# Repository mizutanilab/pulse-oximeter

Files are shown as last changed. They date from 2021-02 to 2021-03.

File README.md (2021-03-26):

# Pulse-oximeter using MAX30102, AAA battery-powered <BR><BR>パルスオキシメーター MAX30102 使用，単４電池駆動
Of course, it's home brewed. もちろん自作です。<br>
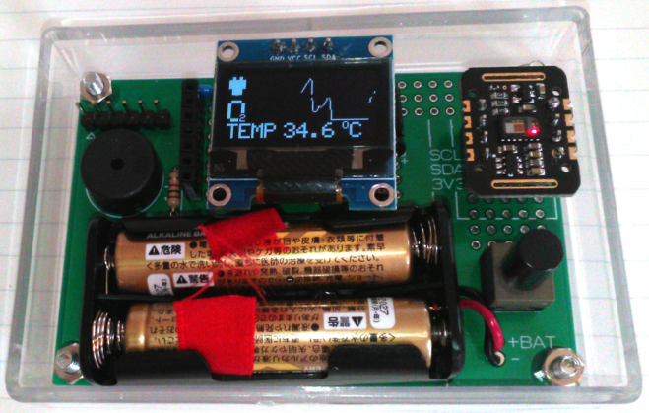
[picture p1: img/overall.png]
overall

  
## Display 表示
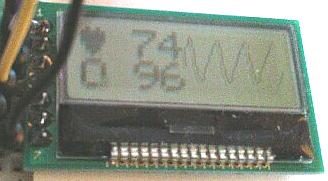
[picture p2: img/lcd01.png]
LCD
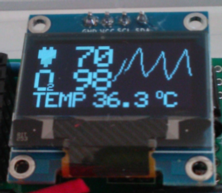
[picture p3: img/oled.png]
OLED
 
<BR>
Obviously, I'm alive. 明らかに生きてます。<BR><BR>

## Schematic 回路図
Nothing special. 普通です。<BR>
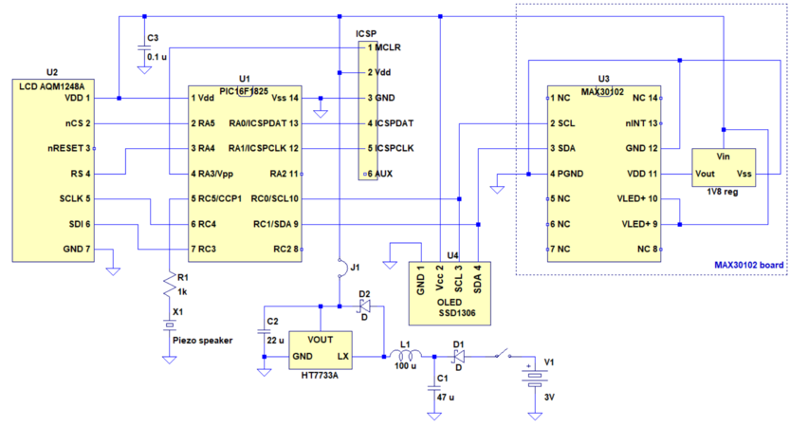
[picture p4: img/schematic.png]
schematic

<BR><BR>

## PCB 基板
Gerber files are <A href="gerber/">here</a>. ガーバーファイルは<a href="gerber/">ここ</a>です。<BR>
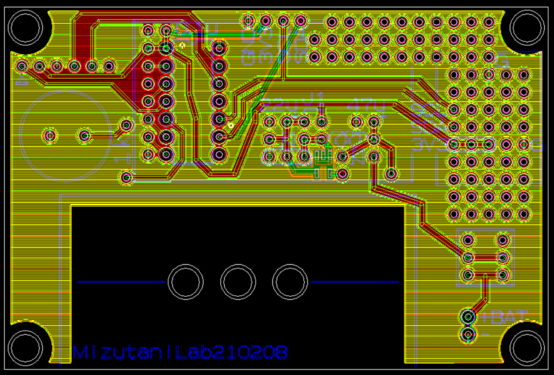
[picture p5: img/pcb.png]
pcb

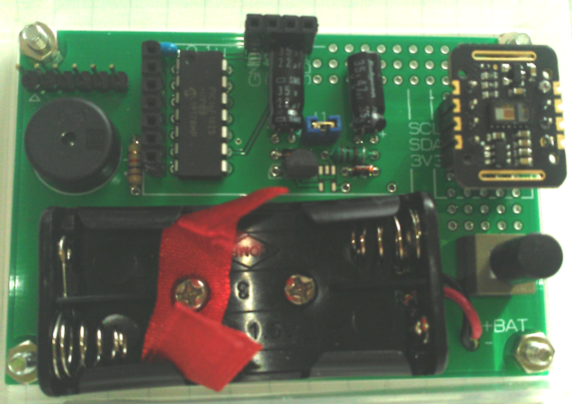
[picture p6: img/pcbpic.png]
pcb_picture

<BR><BR>

## BOM 部品表
<table>
<tr><th>Item</th><th>Description</th><th>Brand</th><th>QTY</th></tr>
<tr><td>Sensor</td><td>MAX30102 breakout</td><td>Maxim Integrated, etc</td><td>1</td></tr>
<tr><td>MCU</td><td>PIC16F1825-I/P</td><td>Microchip</td><td>1</td></tr>
<tr><td>Display</td><td>OLED with SSD1306<BR>or AQM1248A</td><td>Sunhokey, etc<BR>Akizuki</td><td>1</td></tr>
<tr><td>3V3 boost conv</td><td>HT7733A (TO-92)<BR>or TPS613221ADBV, etc</td><td>Holtek<BR>TI</td><td>1</td></tr>
<tr><td>Schottkey D</td><td>SD103A</td><td>PANJIT or Vishay</td><td>2</td></tr>
<tr><td>Piezo speaker</td><td>PKM13EPYH4000-A0</td><td>muRata</td><td>1</td></tr>
<tr><td>L</td><td>100 uH</td><td>-</td><td>1</td></tr>
<tr><td>C</td><td>47 uF electrolytic</td><td>-</td><td>1</td></tr>
<tr><td>C</td><td>22 uF electrolytic</td><td>-</td><td>1</td></tr>
<tr><td>C</td><td>0.1 uF ceramic</td><td>-</td><td>1</td></tr>
<tr><td>R</td><td>1k ohm</td><td>-</td><td>1</td></tr>
<tr><td>SW</td><td>3p toggle or alternate push</td><td>-</td><td>1</td></tr>
<tr><td>Battery box</td><td>AAA x 2</td><td>-</td><td>1</td></tr>
<tr><td>Pin header</td><td>6 pin (ICSP)</td><td>-</td><td>1</td></tr>
<tr><td>Pin header & jumper</td><td>2 pin</td><td>-</td><td>1 each</td></tr>
<tr><td>Pin socket</td><td>7 pin (LCD) or 4 pin (OLED)</td><td>-</td><td>1</td></tr>
<tr><td>Pin socket</td><td>4 pin (MAX30102 board)</td><td>-</td><td>1-2</td></tr>
<tr><td>PCB</td><td>custom</td><td>-</td><td>1</td></tr>
<tr><td>Nuts & bolts</td><td>M3 x 10 mm</td><td>-</td><td>4 sets</td></tr>
<tr><td>Nuts & bolts</td><td>M2.6 x 6 mm</td><td>-</td><td>1-2 sets</td></tr>
<tr><td>Spacer</td><td>3 mm x 3 mm height, resin</td><td>-</td><td>4</td></tr>
<tr><td>Enclosure</td><td>85.5 x 59 x 24 mm, ABS</td><td>Akizuki</td><td>1</td></tr>
</table>
It's less than 25 US$ in total. MAX30102 breakout board with a 1.8V regulator is available from Maxim (MAXREFDES117#) and also from 3rd parties. MAX30101 board can also be used. There are two display options: OLED with SSD1306 and LCD AQM1248A with ST7565R. Choose one of them using #define directive. HEX binary for each display is available. HT7733A is a DC/DC boost converter, which can be substituted with TPS613221ADBV, TPS61097A-33DBV, MAX1724EZK33, or XC9142B33CMR-G. Surface mount pads for these devices are prepared, but not tested. If you use a substitute converter, L/C arrangements and their constants should also be reexamined accroding to datasheet recommendations. You may need a 6-pin male-to-female DuPont wire to connect this PCB to a PIC programmer.<BR><BR>
全部で2500円いきません。MAX30102ボードはMaximのMAXREFDES117#などいくつかの種類が入手可能です。MAX30101のでも使えます。ディスプレイは、秋月グラフィックLCDか、SSD1306のOLEDを選べます。ソースコードの#define文で設定してください。HEXファイルはどちらも用意しています。おもて面のパッドはTPS613221ADBVなどHT7733Aの代替品用で、SOTパッケージのHT7733Aには使えません。センサはアマゾンで、それ以外は秋月で手に入ります。基板をPICプログラマーにつなぐには、6pオスメスケーブル（共立電子QIケーブル6S-6Pなど）も必要です。
<BR>

## SpO<sub>2</sub> calculation 計算式
Four options are implemented. Default is option 1.<BR>
4つあります。既定では1です。<BR>
  1. SpO<sub>2</sub> = -33.437 <i>R</i> + 114.9 (linear approximation of Reynolds et al. (1991) Br J Anaesth 67, 638)<BR>
  2. SpO<sub>2</sub> = -17 <i>R</i> + 104 (User guides & manuals 6409, Maxim Integrated)<BR>
  3. SpO<sub>2</sub> = 1.5958422 <i>R</i><sup>2</sup> -34.6596622 <i>R</i> + 112.6898759 (Application note 6845, Maxim Integrated)<BR>
  4. SpO<sub>2</sub> = -45.060 <i>R</i><sup>2</sup> + 30.354 <i>R</i> + 94.845 (MAX3010x sensor library, SparkFun)<BR>
where <i>R</i> = (AC<sub>red</sub> / DC<sub>red</sub>) / (AC<sub>IR</sub> / DC<sub>IR</sub>).<BR><BR>
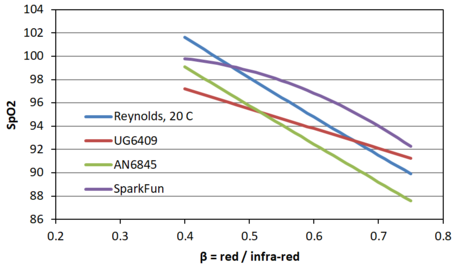
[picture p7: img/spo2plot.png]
spo2models
 <a href="spo2models.xlsx">Excel file</A><BR>

## References 参考
Reynolds et al. (1991) Br J Anaesth 67, 638-643. <a href="https://doi.org/10.1093/bja/67.5.638">DOI</A><BR>
Recommended Configurations and Operating Profiles for MAX30101/MAX30102 EV Kits, <a href="https://www.maximintegrated.com/en/design/technical-documents/userguides-and-manuals/6/6409.html">User guides & manuals 6409</a>, Maxim Integrated<BR>
Guidelines for SpO2 Measurement Using the MaximR MAX32664 Sensor Hub, <a href="https://www.maximintegrated.com/en/design/technical-documents/app-notes/6/6845.html">Application note 6845</a>, Maxim Integrated<BR>
MAX3010x sensor library, SparkFun. <a href="https://github.com/sparkfun/SparkFun_MAX3010x_Sensor_Library">GitHub</a><BR>

## DISCLAIMER お断り
This repository is provided "AS IS", without warranty of any kind, either express or implied. Use it on your own responsibility.<BR>
このリポジトリは「そのまま」で提供されており、明示・暗示を問わず、いかなる保証もありません。ご利用はご自身のご責任でどうぞ。

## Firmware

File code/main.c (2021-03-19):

/* Pulse oximeter 
 * Sensor: MAX30102
 * MCU: PIC16F1823
 * OLED: SSD1306
 * LCD: ST7565R / AQM1248
 * 2021 (C) Mizutani Lab
 */

#include <htc.h>
#include "lcd.h"
#include "i2c.h"
#include "oled.h"

//#define DISP_LCD
#define DISP_OLED

#define MAX30102_INTR_STAT1 0x00
#define MAX30102_INTR_STAT2 0x01
#define MAX30102_INTR_EN1 0x02
#define MAX30102_INTR_EN2 0x03
#define MAX30102_FIFO_WR_PTR 0x04
#define MAX30102_OVF_COUNTER 0x05
#define MAX30102_FIFO_RD_PTR 0x06
#define MAX30102_FIFO_DATA 0x07
#define MAX30102_FIFO_CONFIG 0x08
#define MAX30102_MODE_CONFIG 0x09
#define MAX30102_SPO2_CONFIG 0x0A
#define MAX30102_LED1_PA 0x0C
#define MAX30102_LED2_PA 0x0D
//#define MAX30105_PILOT_PA 0x10
#define MAX30102_MULTI_LED_CTRL1 0x11
#define MAX30102_MULTI_LED_CTRL2 0x12
#define MAX30102_TEMP_INT 0x1F
#define MAX30102_TEMP_FRAC 0x20
#define MAX30102_TEMP_CONFIG 0x21
//#define MAX30105_PROX_INT_THRESH 0x30
#define MAX30102_REV_ID 0xFE
#define MAX30102_PART_ID 0xFF

#define MAX30102_ID 0x15

#define MAX30102_I2C_ADDR 0xAE

char MAX30102getid() {
	return i2c_recv_byte(MAX30102_I2C_ADDR, MAX30102_PART_ID);
}

void MAX30102starttemp(void) {
	i2c_send_byte(MAX30102_I2C_ADDR, MAX30102_INTR_EN2,0x02); //enable temp interrupt
	i2c_send_byte(MAX30102_I2C_ADDR, MAX30102_TEMP_CONFIG,0x01); //start temp
}

void MAX30102init() {
	unsigned char uc_i;
	if (i2c_recv_byte(MAX30102_I2C_ADDR, MAX30102_PART_ID)!= MAX30102_ID) return;
	i2c_send_byte(MAX30102_I2C_ADDR, MAX30102_MODE_CONFIG,0x40); //reset
	for (uc_i=0; uc_i<255; uc_i++) wait2ms();
	i2c_send_byte(MAX30102_I2C_ADDR, MAX30102_FIFO_CONFIG,0x40); //sample avg=4, fifo rollover=false, fifo almost full=32
	i2c_send_byte(MAX30102_I2C_ADDR, MAX30102_MODE_CONFIG,0x03); //0x02 for Red only, 0x03 for SpO2 mode 0x07 for multimode LED
	i2c_send_byte(MAX30102_I2C_ADDR, MAX30102_SPO2_CONFIG,0x27); //SPO2_ADC=4096nA, SPO2 sample rate=100Hz, pulseWidth=411us
	i2c_send_byte(MAX30102_I2C_ADDR, MAX30102_LED1_PA,0x1F); //LED1(IR) 6.2 mA
	i2c_send_byte(MAX30102_I2C_ADDR, MAX30102_LED2_PA,0x1F); //LED2(red) 6.2 mA
	//MAX30102starttemp();
}

unsigned char MAX30102read(unsigned char* pcdata) {
	unsigned char ucDataReady = i2c_recv_byte(MAX30102_I2C_ADDR, MAX30102_FIFO_WR_PTR) - i2c_recv_byte(MAX30102_I2C_ADDR, MAX30102_FIFO_RD_PTR);
	if (ucDataReady) {
		i2c_recv_burst(MAX30102_I2C_ADDR, MAX30102_FIFO_DATA, pcdata, 6);
		pcdata[0] &= 0x03;
		pcdata[3] &= 0x03;
	} 
	return (ucDataReady);
}

unsigned char MAX30102gettemp(char* ctemp, char* ctfrac) {
	unsigned char cRdy = i2c_recv_byte(MAX30102_I2C_ADDR, MAX30102_INTR_STAT2) & 0x02;
	if (cRdy) {
		*ctemp = i2c_recv_byte(MAX30102_I2C_ADDR, MAX30102_TEMP_INT);
		*ctfrac = i2c_recv_byte(MAX30102_I2C_ADDR, MAX30102_TEMP_FRAC);
	}
	return cRdy;
}

#ifdef DISP_LCD
	#define DISP_INIT lcd_init
	#define DISP_CLEAR lcd_clear
	#define DISP_POS lcd_pos
	#define DISP_CHAR lcd_char
	#define DISP_WRITE lcd_write
	#define DISP_CHAR_SCALE lcd_char_scale
#endif
#ifdef DISP_OLED
	#define DISP_INIT oled_init
	#define DISP_CLEAR oled_clear
	#define DISP_POS oled_pos
	#define DISP_CHAR oled_char
	#define DISP_WRITE oled_write
	#define DISP_CHAR_SCALE oled_char_scale
#endif

void disp_string(char* pcstr, char cinv) {
    while (*pcstr) {DISP_CHAR(*pcstr++, cinv);}
}

void disp_string_scale(char* cx, char* cy, char* pcstr, char cscale) {
    while (*pcstr) {DISP_CHAR_SCALE(cx, cy, *pcstr++, cscale);}
}

void disp_hex(unsigned int iout, char idigit) {
	char buf;
	signed char i;
	for (i=3; i>=0; i--) {
		buf = (iout >> (i * 4)) & 0x000f;
		if (buf < 10) buf += 0x30; else buf += 0x37;
		if (i < idigit) DISP_CHAR(buf, 0);
	}
}

void disp_dec2(unsigned char cout, char cinv) {
	//char 8 bit ==> 2 decimal digits
	char buf0, buf1;
	buf0 = cout / 10;
	buf1 = cout - buf0 * 10;
	DISP_CHAR(buf0 + 0x30, cinv);
	DISP_CHAR(buf1 + 0x30, cinv);
}

void disp_dec3(unsigned char cout) {
	//char 8 bit ==> 3 decimal digits
	char buf0, buf1, buf2;
	buf0 = cout / 100; 
	buf1 = cout/10 - buf0 * 10; 
	buf2 = cout - buf1 * 10 - buf0 * 100;
	buf0 += 0x30; if (buf0 == 0x30) buf0 = 0x3a;
	buf1 += 0x30; if ((buf0 == 0x3a)&&(buf1 == 0x30)) buf1 = 0x3a;
	DISP_CHAR(buf0, 0);
	DISP_CHAR(buf1, 0);
	DISP_CHAR(buf2 + 0x30, 0);
}

void disp_dec2scale(char* cx, char* cy, unsigned char cout, unsigned char cscale) {
	//char 8 bit ==> 2 decimal digits
	char buf0, buf1;
	buf0 = cout / 10;
	buf1 = cout - buf0 * 10;
	DISP_CHAR_SCALE(cx, cy, buf0 + 0x30, cscale);
	DISP_CHAR_SCALE(cx, cy, buf1 + 0x30, cscale);
}


void disp_dec3scale(char* cx, char* cy, unsigned char cout, unsigned char cscale) {
	//char 8 bit ==> 3 decimal digits
	char buf0, buf1, buf2;
	buf0 = cout / 100; 
	buf1 = cout/10 - buf0 * 10; 
	buf2 = cout - buf1 * 10 - buf0 * 100;
	buf0 += 0x30; if (buf0 == 0x30) buf0 = 0x3a;
	buf1 += 0x30; if ((buf0 == 0x3a)&&(buf1 == 0x30)) buf1 = 0x3a;
	DISP_CHAR_SCALE(cx, cy, buf0, cscale);
	DISP_CHAR_SCALE(cx, cy, buf1, cscale);
	DISP_CHAR_SCALE(cx, cy, buf2 + 0x30, cscale);
}

void disp_dec5(unsigned int iout, int* pidigit, char csel) {
	//char 8 bit ==> 5 decimal digits
	int i;
	int idiv = 10000;
	int iomit = 1;
	*pidigit = 0;
	for (i=0; i<5; i++) {
		char buf0 = iout / idiv;
		char cinv  = (csel == i) ? 1 : 0;
		if (iomit && (i != 4)) {
			if (buf0) {DISP_CHAR(buf0 + 0x30, cinv); iomit = 0; (*pidigit)++;}
			else DISP_CHAR(' ', cinv);
		} else {
			DISP_CHAR(buf0 + 0x30, cinv);
			(*pidigit)++;
		}
		if (i==4) break;
		iout = iout - buf0 * idiv;
		idiv /= 10;
	}
}

void init(void){
	////ANSELs
	ANSELA = 0x00; //set as digital
	ANSELC = 0x00;
	////Weak pull ups
	WPUC = 0x00;//disable WPUC<5:0>
	WPUA = 0x00;//disable WPUA
	nWPUEN = 0;//enable indiv WPU bits
	////CPU clock oscillator
	//SCS1 = 1; SCS0 = 0; //SCS<1:0> = 1x (use internal clock)
	//set config bits FOSC<2:0> = 100 (use internal clock)
	//IRCF3 = 0; IRCF2 = 1; IRCF1 = 1; //default: IRCF<3:0> = 0111 (500 kHz)
	//IRCF3 = 1; IRCF2 = 1; IRCF1 = 1; IRCF0 = 1; // IRCF<3:0> = 1111 (16 MHz)
	SCS1 = 0; SCS0 = 0; //SCS<1:0> = 00 for PLL
	IRCF3 = 1; IRCF2 = 1; IRCF1 = 1; IRCF0 = 0; // IRCF<3:0> = 1110 (8 MHz)
	SPLLEN = 1;//enable 4x PLL => 8 MHx x 4
	////CCP1 (beep)
	TRISC5 = 0;//enable RC5/P1A output
//	TRISC4 = 0;//enable RC4/P1B output
	CCPTMRSbits.C1TSEL1 = 0; //use timer2 for CCP1
	CCPTMRSbits.C1TSEL0 = 0;
//	PR2 = 0x3D;//2.05 kHz
//	CCPR1L = 0x1F;//2.05 kHz, 50.0%duty
	PR2 = 0x19;//5.0 kHz
	CCPR1L = 0x0C;//5.0 kHz, 50.0%duty
	T2CONbits.T2CKPS1 = 1;//prescale 1/64
	T2CONbits.T2CKPS0 = 1;
	T2CONbits.TMR2ON = 1;
	P1M1 = 0;//PWM single output
	P1M0 = 0;
	CCP1M3 = 1;//enable CCP1 module in PWM mode
	CCP1M2 = 1;
	CCP1M1 = 0;
	CCP1M0 = 0;
	STR1A = 0;//output P1A (beep)
	STR1B = 0;//disable P1B
	STR1C = 0;//disable P1C
	STR1D = 0;//disable P1D
	//timer1 to stop beep
	T1GCONbits.TMR1GE = 0;//disable timer1 gating
	T1CONbits.TMR1ON = 0;//disable timer1
	T1CONbits.TMR1CS0 = 0;//timer1 clock = Fosc/4
	T1CONbits.TMR1CS1 = 0;
	T1CONbits.T1CKPS0 = 1;//timer1 1/8 prescaler
	T1CONbits.T1CKPS1 = 1;
	TMR1H = 0;//reset timer1
	TMR1L = 0;
	PIE1bits.TMR1IE = 1;//enable timer1 interrupt
	INTCONbits.PEIE = 1;//enable peripheral interrupt
	//MAX30102
	i2c_init();
	MAX30102init();
	//display
	DISP_INIT();
	DISP_CLEAR();
	//
//	oled_init();
//	oled_clear();
//	oled_pos(0, 0);
//	oled_char('A', 0);
//	oled_pos(20, 1);
//	oled_char('B', 0);
//	oled_pos(70, 3);
//	oled_char('C', 0);
//	unsigned char uc_x, uc_y;
//	uc_x = 80; uc_y = 0;
//	oled_char_scale(&uc_x, &uc_y, 'D', 3);
}

void interrupt isr(void){
	if (PIR1bits.TMR1IF) {
		PIR1bits.TMR1IF = 0;
		T1CONbits.TMR1ON = 0;
		STR1A = 0;
	}
}

unsigned short uc_prevwave;
void plotWave(unsigned char ucStart, unsigned char uc_wave) {
	unsigned char uc_y;
	unsigned char uc_dot;
	unsigned char uc_disp, uc_pos;
	unsigned char uc1, uc2;
	if (ucStart == 0) uc_prevwave = uc_wave;
	if (uc_wave > uc_prevwave) {uc1 = uc_wave; uc2 = uc_prevwave+1;}
	else if (uc_wave < uc_prevwave) {uc2 = uc_wave; uc1 = uc_prevwave-1;}
	else {uc2 = uc_wave; uc1 = uc_prevwave;}
	for (uc_y=0; uc_y<6; uc_y++) {
		uc_disp = 0;
		for (uc_dot=0; uc_dot<8; uc_dot++) {
			uc_pos = (5-uc_y)*8 + (7-uc_dot);
			if ((uc_pos >= uc2)&&(uc_pos <= uc1)) uc_disp |= (0x1 << uc_dot);
		}
		DISP_POS(64+ucStart, uc_y);
		DISP_WRITE(uc_disp, 1);
	}
	uc_prevwave = uc_wave;
}
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

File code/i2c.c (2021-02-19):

/*
 *	I2C interface
 *	2016-2021 (C) Mizutani Lab
 */

#include	<htc.h>
#include	"i2c.h"
//#include	"lcd.h"

//#define I2C_SCL_OUT LATCbits.LATC0
//#define I2C_SCL_IN PORTCbits.RC0
#define I2C_SCL_TRIS TRISCbits.TRISC0
#define I2C_SCL_PULLUP WPUCbits.WPUC0
//#define I2C_SDA_OUT LATCbits.LATC1
//#define I2C_SDA_IN PORTCbits.RC1
#define I2C_SDA_TRIS TRISCbits.TRISC1
#define I2C_SDA_PULLUP WPUCbits.WPUC1

//SI5351A address
//#define I2C_ADDR 0xC0
//MAX30102 address
//#define I2C_ADDR 0xAE

void i2c_init(void) {
	//ANSELC = 0x00; //set as digital
	I2C_SCL_PULLUP = 1;
	I2C_SDA_PULLUP = 1;
	I2C_SCL_TRIS = 1;//disable output
	I2C_SDA_TRIS = 1;//disable output
	//SSP1ADD = 0x4F;//Baud rate 100 kHz
	SSP1ADD = 0x13;//Baud rate 400 kHz
	SSP1STAT = 0x00;//SMP=0 (Slew rate control enabled for high speed mode), CKE=0 (Disable SMbus specific inputs)
	SSP1CON1 = 0x28;//SSPEN=1 (Enable SSP unit), SSP1M<3:0>=1000 (I2C master)
}

void i2c_start(void) {
	SSP1CON2bits.SEN = 1;
	while(SSP1CON2bits.SEN);
}

void i2c_restart(void) {
	PIR1bits.SSP1IF = 0;
	SSP1CON2bits.RSEN = 1;
	while(SSP1CON2bits.RSEN);
}

void i2c_stop(void) {
	SSP1CON2bits.PEN = 1;
	while(SSP1CON2bits.PEN);
}

void i2c_write(unsigned char byte) {
	PIR1bits.SSP1IF = 0;
	SSP1BUF = byte;
	while(SSP1STATbits.R_nW);
	//while(!PIR1bits.SSP1IF);
}

char i2c_read(char bLastRx) {
	PIR1bits.SSP1IF = 0;
	SSP1CON2bits.RCEN = 1;
	while(SSP1CON2bits.RCEN);
	//ack sequence
	if (bLastRx) SSP1CON2bits.ACKDT = 1; else SSP1CON2bits.ACKDT = 0;
	SSP1CON2bits.ACKEN = 1; while (SSP1CON2bits.ACKEN);
	//
	return SSP1BUF;
}

void i2c_send_byte(unsigned char i2cAddr, unsigned char reg, unsigned char data) {
	i2c_start();
	i2c_write(i2cAddr);
	i2c_write(reg);
	i2c_write(data);
	i2c_stop();
}

void i2c_send_burst(unsigned char i2cAddr, unsigned char reg, unsigned char* pcdata, unsigned char ndata){
	i2c_start();

	i2c_write(i2cAddr);
	i2c_write(reg);
	unsigned char i;
	for (i=0; i<ndata; i++) {i2c_write(pcdata[i]);}

	i2c_stop();
}

unsigned char i2c_recv_byte(unsigned char i2cAddr, unsigned char reg) {
	unsigned char ucRtn;
	i2c_start();
	i2c_write(i2cAddr);// I2C slave address
	i2c_write(reg);// Send register address
	i2c_restart();
	i2c_write(i2cAddr | 0x01);// I2C slave address + read flag
	ucRtn = i2c_read(1);// receive data
	i2c_stop();
	return ucRtn;
}

void i2c_recv_burst(unsigned char i2cAddr, unsigned char reg, unsigned char* pcdata, unsigned char ndata){
	i2c_start();
	i2c_write(i2cAddr);//address, write
	i2c_write(reg);
	i2c_restart();

	i2c_write(i2cAddr | 0x01);// I2C slave address + read flag
	unsigned char i;
	for (i=0; i<ndata; i++) {pcdata[i] = i2c_read(i == ndata-1);}
	i2c_stop();
}
